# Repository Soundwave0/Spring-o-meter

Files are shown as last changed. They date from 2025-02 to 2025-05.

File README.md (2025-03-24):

## Spring-O-Meter1000
**Ensure that ESP is configured in Arduino IDE with ESPduino package** <br>
https://arduino.esp8266.com/stable/package_esp8266com_index.json <br> in arudino IDE add the following path <br>
# Introduction

Presented here is the device Spring-O-Meter 1000, created for the class FMDII at the faculty of Mechatronics. The aim of this project was to measure the spring constant in both tension and compression springs by building some device. Being a Mechatronic device it contains Electrical, Software and Mechanical Components that work in synchrony. The following documentation will contain a description of the 3 components as well as the usage of the device. For the the Step and Program Files go to  
https://github.com/Soundwave0/Spring-o-meter.git

# Specifications

| Spec | Value | Unit |
|------|-------|------|
| Range Comp. | 90 | mm |
| Range Ten. | 115 | mm |
| MAX Comp pos | 110 | mm |
| MIN Comp. pos | 20 | mm |
| MAX Ten. pos | 135 | mm |
| MIN Ten. pos | 10 | mm |
| Max Comp. Di | 19 | mm |
| Min Comp. Di | 3 | mm |
| MAX force | 9.806 | N |
| MAX cal. weight | 950 | g |
| Min cal. weight | 3 | g |
| Disp per Rotation | 2 | mm |
| Gear Ratio(lead:enc.) | 1:3 |  |
| Encoder Disp. Resolution | 0.022 | mm |
| Force sensor Accuracy | ≈0.1 | % |
| K Accuracy | ≈0.015 | N/mm |

# Usage

1. Download the Spring-O-Meter GUI code either from the git-hub link or install from the executable (if you face any issues in the git-hub version try turning off signing)
2. Plug in the Micro-USB cable into the Spring-O-Meter and then into the USB port in your computer, see if the blue led begins to shine through the support on the bottom. Remember if your Micro-USB cable does not have data transfer capabilities it will turn on but no serial communication will be possible
3. Go to Device Manager-> Ports and check to see if you can see the Silicon Labs CP210x, remember the COM port it is connected to 
4. Launch the GUI and click on "COM Configuration" and select the COM that you found in the previous step
5. Press Check COM if it informs you that everything is good then continue if not restart the application and recheck the COM in device manager
6. If you would like to Calibrate your sensor then turn on Calibration , wait until the button settles then place your Spring-O-Meter on its head then press "Calibrate Zero", after this enter the weight of your test weight then place it, then press "Complete Calibration". Once this button is changed to "Calibrated" continue
7. If you don't want to Calibrate but instead want to use a previous value of Calibration taken from EEPROM, then press Use Prev Cal instead of doing Step 6
8. Next place your Spring-O-Meter in the testing Position, install your spring and press tare, then reset 
9. If you would like to measure the point at which the spring begins to exert a force on the sensor to set your zero better, turn on the kickpoint by pressing the button next to kickpoint label turning the OFF to ON. Move the Stage to tense or compress the spring until the kickpoint is no longer null. Once this happens, move your stage to kick point, tare and reset
10. Now you can begin sampling, move your stage a bit, wait for the measurement to settle then press sample, repeat for desired number of samples then press Graph Spring
11. To reset everything and repeat another trial click New Trial

# Parts

## Stock-Parts

| NAME | SPEC | QTY |
|------|------|-----|
| LSU |  | 1 |
| ESP8266 | NodeMCU 12-E | 1 |
| Encoder 30IMP | KY-040 | 1 |
| Load-Cell 1Kg | NA27 | 1 |
| Load-Cell Amp | HX711 | 1 |
| M2.5x40 |  | 2 |
| M6x12 | ISO4762 | 4 |
| M2.5 pin |  | 1 |
| micro-USB cable | W/ Data Bus | 1 |
| Breadboard cables |  | 12 |

## 3D printed parts

| NAME | SPEC | QTY |
|------|------|-----|
| Spur Gear1 | 3d printed | 1 |
| Spur Gear Clamp | 3d printed | 1 |
| Spur Gear 2 | 3d printed | 1 |
| Base 1 | 3d printed | 1 |
| Base 2 | 3d printed | 1 |
| Base Lid | 3d printed | 1 |
| Cable Lid | 3d printed | 1 |
| Clamp | 3d printed | 1 |
| Plate Big | 3d printed | 1 |
| Plate Small Gear | 3d printed | 1 |
| Plate Small | 3d printed | 1 |

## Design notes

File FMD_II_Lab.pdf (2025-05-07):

### course FMDII

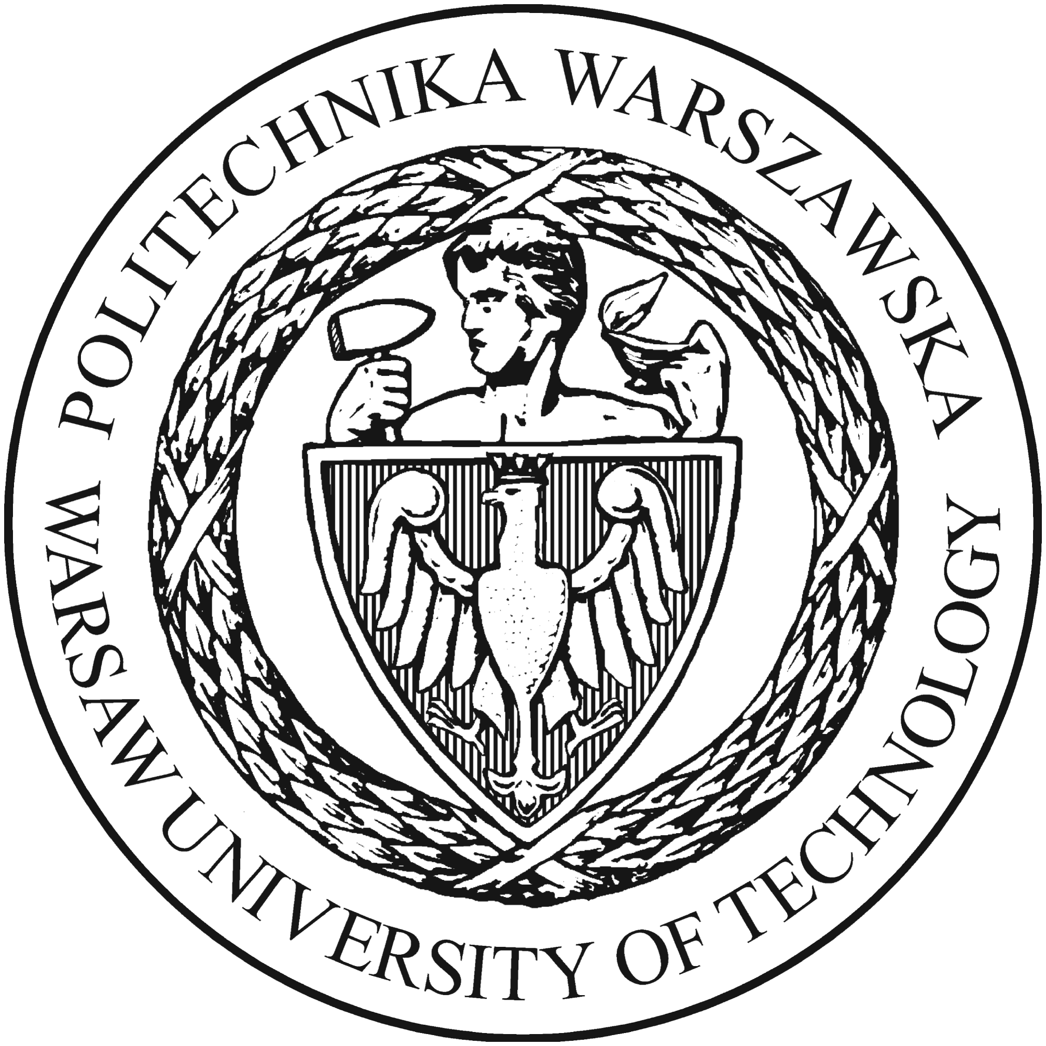
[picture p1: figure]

### Spring-O-Meter 2000

Spring Measurement Device

# Konrad Kosuge, Pawel Seroka

student record book number

supervisor
Dr. Ksawery Sziekedans

WARSAW March 2025

## Contents

1. Introduction | | 2
2. Specifications | | 2
3. Usage | | 3
4. Parts | | 4
4.1. Stock-Parts | | 4
4.2. 3D printed parts | | 4
4.2.1. Spur Gears | | 5
4.2.2. Spur Gear Clamp | | 5
4.2.3. Supports | | 5
4.2.4. Plates | | 5
4.2.5. Clamp | | 5
5. Mechanical Implementation | | 6
5.1. Gearing | | 6
5.2. Force Sensor | | 6
5.3. LSU | | 6
5.4. Mechanism | | 6
6. Electrical Implementation | | 7
6.1. Encoder | | 7
6.2. Force Sensor | | 8

### 7. Software Implementation | 10

7.1. Serial COM Protocol | 10
7.2. ESP 8266 | 11
7.3. GUI | 16
7.4. GUI Backend | 16
7.5. GUI Frontend | 22

### 8. Test | 22

## 1. Introduction

Presented here is the device Spring-O-Meter 1000, created for the class FMDII at the faculty of Mechatronics. The aim of this project was to measure the spring constant in both tension and compression springs by building some device. Being a Mechatronic device it contains Electrical, Software and Mechanical Components that work in synchrony. The following documentation will contain a description of the 3 components as well as the usage of the device. For the the Step and Program Files go to https://github.com/Soundwave0/Spring-o-meter.git

## 2. Specifications

Spec | Value | Unit
Range Comp. | 90 | mm
Range Ten. | 115 | mm
MAX Comp pos | 110 | mm
MIN Comp. pos | 20 | mm
MAX Ten. pos | 135 | mm
MIN Ten. pos | 10 | mm
Max Comp. Di | 19 | mm
MIN Comp. Di | 3 | mm
MAX force | 9.806 | N
MAX cal. weight | 950 | g
MIN cal. weight | 3 | g
Disp per Rotation | 2 | mm
Gear Ratio(lead:enc.) | 1:3
Encoder Disp. Resolution 0.022 | mm
Force sensor Accuracy | ≈0.1 | %
K Accuracy | ≈0.015 N/mm

## 3. Usage

1. Download the Spring-O-Meter GUI code either from the git-hub link or install from the executable (if you face any issues in the git-hub version try turning off signing)
2. Plug in the Micro-USB cable into the Spring-O-Meter and then into the USB port in your computer, see if the blue led begins to shine through the support on the bottom. Remember if your Micro-USB cable does not have data transfer capabilities it will turn on but no serial communication will be possible
3. Go to Device Manager-> Ports and check to see if you can see the Silicon Labs CP210x, remember the COM port it is connected to
4. Launch the GUI and click on "COM Configuration" and select the COM that you found in the previous step
5. Press Check COM if it informs you that everything is good then continue if not restart the application and recheck the COM in device manager
6. If you would like to Calibrate your sensor then turn on Calibration , wait until the button settles then place your Spring-O-Meter on its head then press "Calibrate Zero", after this enter the weight of your test weight then place it, then press "Complete Calibration". Once this button is changed to "Calibrated" continue
7. If you don’t want to Calibrate but instead want to use a previous value of Calibration taken from EEPROM, then press Use Prev Cal instead of doing Step 6
8. Next place your Spring-O-Meter in the testing Position, install your spring and press tare, then reset
9. If you would like to measure the point at which the spring begins to exert a force on the sensor to set your zero better, turn on the kickpoint by pressing the button next to kickpoint label turning the OFF to ON. Move the Stage to tense or compress the spring until the kickpoint is no longer null. Once this happens, move your stage to kick point, tare and reset
10. Now you can begin sampling, move your stage a bit, wait for the measurement to settle then press sample, repeat for desired number of samples then press Graph Spring
11. To reset everything and repeat another trial click New Trial

## 4. Parts

### 4.1. Stock-Parts

NAME | SPEC | QTY
LSU | | 1
ESP8266 | NodeMCU 12-E 1
Encoder 30IMP | KY-040 | 1
Load-Cell 1Kg | NA27 | 1
Load-Cell Amp | HX711 | 1
M2.5x40 | | 2
M6x12 | ISO4762 | 4
M2.5 pin | | 1
micro-USB cable | W/ Data Bus | 1
Breadboard cables | | 12
4.2. 3D printed parts
NAME | SPEC | QTY
Spur Gear1 | 3d printed 1
Spur Gear Clamp 3d printed 1
Spur Gear 2 | 3d printed 1
Base 1 | 3d printed 1
Base 2 | 3d printed 1
Base Lid | 3d printed 1
Cable Lid | 3d printed 1
Clamp | 3d printed 1
Plate Big | 3d printed 1
Plate Small Gear | 3d printed 1
Plate Small | 3d printed 1

4. Parts

### 4.2.1. Spur Gears

Parts (Spur Gear 1 and Spur Gear 2)used in gearing mechanism.

### 4.2.2. Spur Gear Clamp

Clamp is used to fix the Spur Gear 2 onto the screw shaft and prevent it from sliding on the thread by tightening with screws.

### 4.2.3. Supports

Base 1 with Base Lid is used to hide the electronics (amplifier,esp controller). Com-bined with Base 2 it lifts the device so that there is clearance between ground and the moving gears.

### 4.2.4. Plates

Plate Big is used to provide mounting point for the force sensor and to hide cables in the space inside it, closed by the Base Lid.
Plate Small is used as a mounting point for the springs.
Plate Small Gear is used to mount angle sensor with a Spur Gear 1 attached to it.

### 4.2.5. Clamp

Clamp is used to provide attachment point for the springs to the force sensor.

## 5. Mechanical Implementation

### 5.1. Gearing

To measure the rotation of the screw shaft we need to be connect it to the sensor. This can be obtained by using belts, chains or gears. For this project we chose the gear system, due to ease of obtaining gears by 3D printing. Additionally we introduced the gear ratio to improve sensor accuracy. Sensor has 30 impulses per rotation and this causes uncertainty of 12◦
. By introducing a gear ratio equal to 3, we triple the number of pulses per screw shaft rotation. This changes the uncertainty to 4◦

### 5.2. Force Sensor

Force sensor is fixed by screws on to the plate and its purpose is to measure the force applied to the spring.

### 5.3. LSU

Linear stage unit is used to deflect springs with good precision. It acts as a basis in our device to which all the components are mounted. Additionally it enables to maintain the deflection of the spring without additional mechanism.

### 5.4. Mechanism

The idea behind the design is that by turning the threaded shaft the gears are turned with it encoding the rotated angle on the encoder that multiples it by constant (around 0.00185 mm/degree of turn). In this way we obtain the length by which spring is deflected. When the threaded shaft is turned the table is moved and with it the Big Plate causing the offset of the force sensor to which the spring is attached to. This enables the deflection force to be measured. Deflection distance and force information is then sent to the esp controller where it can be processed to provide the spring constant.

## 6. Electrical Implementation

### 6.1. Encoder

KY-040 model, Connecting the Digital Data pins to the ESP and using the CLK to generate the timing pulses to determine the direction of rotation of position for further detail look at the code in the esp8266.

KY-040
Parameter | Specification | Unit
General
Type | Mechanical Incremental Rotary Encoder -
Resolution | 20 pulses per revolution (PPR) | -
Operating Voltage | 5V (3.3V compatible) | V
Current Consumption <10 | mA
Mechanical
Shaft Type | 6mm D-shaped with push button | -
Rotation Life | 100,000 | cycles
Switch Life | 50,000 | cycles
Electrical
Output Type | Quadrature (A/B phase) + Switch | -
Output Signal | Digital (TTL compatible) | -
Debounce Circuit | Included (RC filter) | -
Physical
Module Dimensions | 30 × 19 × 30 | mm
Shaft Length | 15 | mm
Performance
Maximum RPM | 100 | RPM
Contact Resistance | <50 | m
Environmental
Operating Temp | -25 to +70 | °C

Pin Configuration:

1. CLK (A phase output)
2. DT (B phase output)
3. SW (Push button switch)
4. VCC (3.3-5V power supply)
5. GND (Ground)

6. Electrical Implementation

### 6.2. Force Sensor

Load cell NA27 is connected to the HX711 load cell amplifier. The amplifier is connected to the ESP8266 and the code reads the output of the amplifier and determines the force on the sensor. The HX711 interfaces the ESP8266 through the HX711 ADC library. Ensure that the pin that supplies the voltage for the force sensor is the Vin pin since this is the only one that can power 5 Volts. (Force Sensor takes in between 5-12V for proper functionality)

HX711
Parameter | Specification | Unit
General
ADC Type | 24-bit Sigma-Delta | -
Sampling Rate | 10 or 80 (selectable) | SPS
Supply Voltage | 2.6 - 5.5 | V
Operating Current | < 1.5 | mA
Input
Differential Input | ±20mV (PGA=128), ±80mV (PGA=64) | mV
PGA Gain | 128 (default), 64 (selectable) | -
Output
Interface | Serial (2-wire) | -
Data Rate | 10Hz (80Hz noise) or 80Hz (10Hz noise) Hz
Load Cell Support
Excitation Voltage | 5 | V
Recommended Load Cells 1kg, 5kg, 10kg, 20kg | -
Physical
Dimensions | 34 × 17 | mm
Pin Count | 16 | -
Performance
Resolution | 1 in 16,777,216 | counts
Noise (PGA=128) | 0.5 | V RMS ˜
Non-linearity | ±0.01 | % FS
Temperature
Operating Range | -40 to +85 | °C

6. Electrical Implementation

NA27
Rated Capacities | 0.61235610kg
Rated Output | 1.0 ±0.15mV/V
Zero Balance | ±0.1000 mV/V
Non-linearity | 0.03 %R.O.
Hysteresis | 0.03 %R.O.
Repeatability | 0.03 %R.O.
30mins Creep | 0.03 %R.O.
30mins Return | 0.03 %R.O.
Safe Overload | 150 %R.O.
Ultimate Overload | 200 %R.O.
Temperature Effect On Output | 0.01 %R.O./°C
Temperature Effect On Zero | 0.05 %R.O./°C
Input Impedance | 1115±10%
Output Impedance | 1000±10%
Insulation Impedance | 2000 M/(50VDC)
Recommended Excitation | 512 VDC ˜
Maximum Excitation | 15 VDC
OperatingTemperatureRange | -2060 °C ˜
Construction | Aluminum Alloy
Protection Class | IP65
Cable | 0.8×0.25m
Recommended Platform Size | 150×150 mm
Mode of Connection | RedEXC+,BlackEXC-,GreenSIG+,WhiteSIG-

## 7. Software Implementation

### 7.1. Serial COM Protocol

A protocol specifically programmed for this device, the Application can send requests or data over the serial port to the device, and the device can send requests or data over the serial port to the Application. The table features how the Application and the ESP communicate with each other.

Command Description | Expected Response
ONN | Turn on calibration, LED turns on | -
OFF | Turn off calibration, LED turns off | -
WGH | Get the force signal | Force value
POS | Get the position | Position value
IMP | Get the impulse counter | Impulse counter value
COM | Test COM port connection | "OK"
RST | Reset the position | "SUC"
TRE | Tare the scale | "SUC"
CAL | Calibrate the weight | -
TREF | Tare fast during measurement | -
ERR | Error value received when request is invalid | Error message
CALVAL | Change the calibration value in the ESP program -
APUL | Application pulls from microcontroller EEPROM EEPROM data
MPUL | Microcontroller gets value from application | Value from application

7. Software Implementation

### 7.2. ESP 8266

#include<HX711_ADC.h>

#include <EEPROM.h>

//global variables for position encoder
const int pinA = 5;// Connected to CLK on KY040 D1 const int pinB = 4; // Connected to DT on KY040 D2 //global variables for the force sensor
const int pinSCK = 14;//D5
const int pinDT = 12;//D6
//global variables for position encoder functionality

const double impulses = 30;
const double distance_per_rotation = 3.2;//change after measurement

const double gear_ratio = 4;
int encoderPosCount = 0;
int pinALast;
int aVal;
boolean bCW;
const double distance_per_impulse = (1/impulses)*(distance_per_rotation)/gear_ratio;

float plat_pos = 0;
//global variables for force sensor
HX711_ADC LoadCell(pinDT,pinSCK);

boolean _tare = true;
unsigned long t =0;
float calibrationValue =100;
unsigned long stabilizingtime = 3000;//increasing the accuracy of the tare operation by increasing the value

float weight_value = 0;
const int samples = 10;//sampling during filtering and averaging for returning the signal
//global varaibles for communication protocol

String com_data;
// for the EEPROM
double calibrationmap10X5 = 1; //Variable to store data read from EEPROM. int eepromAddress = 0; //address in EEPROM to read and write
int EEPROM_SIZE = 512;//EERPROM SIZE
void encoder_position_reader();//function to read the position of the encoder void com_functions();//function for the communication protocol
void HX711_Loop();//Function for force sensor loop

void setup()
{
pinMode (pinA,INPUT);//Defining pin modes pinMode (pinB,INPUT);

pinMode(LED_BUILTIN, OUTPUT);
pinALast = digitalRead(pinA);
Serial.begin (9600);//Serial begin the Baud rate delay(10);
LoadCell.begin();//Starting the load cell LoadCell.start(stabilizingtime, _tare); LoadCell.setSamplesInUse(samples);
// EEPROM calibration storage EEPROM.begin(EEPROM_SIZE);
}
void loop()
{
com_functions();//Check for communication between application and ESP in serial and respond accordingly encoder_position_reader();//Read encoder position
HX711_Loop();//Read Force
}
void HX711_Loop()
{
LoadCell.update();
weight_value = LoadCell.getData(); }
//Helper Functions
void com_functions()
{
if(Serial.available())
{
com_data = Serial.readStringUntil(’\n’); if(com_data=="ONN")
{
digitalWrite(LED_BUILTIN,LOW); }
else if(com_data == "OFF")
{
digitalWrite(LED_BUILTIN, HIGH); }
else if(com_data == "COM")
{
Serial.write("OK\n");
}
else if(com_data == "XRC") {

}
else if(com_data == "POS") // function to get the position of the platform

{
String myString = String(plat_pos); //Serial.println(plat_pos);
char* buf1 = (char*) malloc(sizeof(char)*myString.length()+1); myString.toCharArray(buf1, myString.length()+1); Serial.write(buf1);
free(buf1);
Serial.write(’\n’);
}
else if(com_data == "IMP")
{
String myString = String(encoderPosCount);
char* buf2 = (char*) malloc(sizeof(char)*myString.length()+1); myString.toCharArray(buf2, myString.length()+1); Serial.write(buf2);
free(buf2);
Serial.write(’\n’);
}
else if(com_data == "RST")//resets the position on the encoder to 0 {

plat_pos = 0;
encoderPosCount = 0;
Serial.write("SUC");
Serial.write(’\n’);
}
else if(com_data == "CALVAL")//pulls the calibration constant from the gui and sets it in the application part {
Serial.write("CALRQS\n");//implement in c# part
//Serial.write(’\n’);
String calibration_value_string = Serial.readStringUntil(’\n’); float calibration_value = calibration_value_string.toFloat();

calibrationValue = calibration_value;
}
else if(com_data == "TRE")//more accuarate slower tare {
LoadCell.tare();
Serial.write("SUC\n");
}
else if(com_data == "CAL")//preforms the calibration operation {
LoadCell.setCalFactor(calibrationValue); Serial.write("SUC");
Serial.write(’\n’);
}

else if (com_data == "TREF")//tare fast {
LoadCell.tareNoDelay();
}
else if(com_data == "WGH")//send the weight {
String myString = String(weight_value); //Serial.println(weight_value);
char* buf3 = (char*) malloc(sizeof(char)*myString.length()+1); myString.toCharArray(buf3, myString.length()+1); Serial.write(buf3);
free(buf3);
Serial.write(’\n’);
}
else if(com_data == "MPUL")//Micro-controller pulls data from application application data -> Micro-Controller {
//send request to application
Serial.write("MAPREQ");//send calibrationmap request to application Serial.write(’\n’);
//receive value
String calibration_value_string = Serial.readStringUntil(’\n’); calibrationmap10X5 = calibration_value_string.toDouble(); //write value to memory
EEPROM.put(eepromAddress,calibrationmap10X5); EEPROM.commit();
}
else if(com_data == "APUL")//Application pulls data from microcontroller Micro-controller -> Application {
double calmap;//write to eeprom when power is on but when off will chnage vlaue to 16711680 (weird) EEPROM.get(eepromAddress,calmap);
String myString = String(calmap);
char* buf = (char*) malloc(sizeof(char)*myString.length()+1); myString.toCharArray(buf, myString.length()+1); Serial.write(buf);
free(buf);
Serial.write(’\n’);
}

else
{
Serial.write("ERR\n");
}
}
}
void encoder_position_reader()

{
aVal = digitalRead(pinA);
if (aVal != pinALast )
{
if (digitalRead(pinB) != aVal) {

encoderPosCount ++;
bCW = true;
}

else
{

bCW = false;
encoderPosCount--;
}
if (bCW){}
else{}

plat_pos = distance_per_impulse*encoderPosCount; }

pinALast = aVal;
}

Above is the code that is flashed to the ESP8266 It contains

1. Setup of the pins
2. Setup of the HX711 Force reading
3. Variables to keep track of the data
4. Encoder position reading
5. Communication Protocol Implementation

### 7.3. GUI

### 7.4. GUI Backend

using System;
using System.Collections.Generic; using System.Collections.Specialized; using System.ComponentModel;
using System.Data;
using System.Diagnostics;
using System.Drawing;
using System.Drawing.Text;
using System.Linq;
using System.Reflection;
using System.Security.Cryptography.X509Certificates; using System.Security.Permissions;
using System.Text;
using System.Threading.Tasks;
using System.Windows.Forms;
using System.Windows.Forms.DataVisualization.Charting;

namespace Spring_o_meter
{

public partial class Form1 : Form
{
//initializing values for calibration
private double signal_zero_state_calibration = 0; private double signal_test_weight_calibration = 0; private double to_force_map = 0;
Boolean calibrated = false;

//initalizing values for reading //idea of using structs for this purpose public struct data_trial
{

public data_trial(double pos, double force) {
Pos = pos;
Force = force;
}
public double Pos { get; set; }
public double Force { get; set; }
}
data_trial current_data = new data_trial();//made null just in case
data_trial prev_data = new data_trial();
Stack<data_trial> data_trial_stack = new Stack<data_trial>();// will store the data in stack format private double spring_k = 0;
private double mean_k = 0;
private double sum = 0;
// for position component
private const double GEAR_RATIO = 3;//between driver and gear
private const double DISTANCE_PER_ROTATION = 2; // distance in mm of distance per rotation private const double IMPULSES_PER_ROTATION = 30;// impulses in the encoder
//for the graph
private const int k_stack_reading_depth = 5;// stack reading depth for graphing trials private Stack<double> stack_k = new Stack<double>(); // stack that stores the spring constants

private int sample_count = 0;
//for the port
private string port = "NULL";
Boolean com_connected = false;
private Boolean kickpoint = false; private Boolean kickpoint_found = false;
private double kickpoint_value = 0.15;
private double sigweight;
private double Impulse_to_position(double encoder_count)

{
return (1 / IMPULSES_PER_ROTATION) * (DISTANCE_PER_ROTATION / GEAR_RATIO) * encoder_count; }
void reset()// implement rest function
{
Get_STM("STM");
}
private void Force_Calibration()
{
if (calibration_Toggle.Text == "ON" && com_connected)

{
serialPort1.WriteLine("WGH");
signal_test_weight_calibration = Convert.ToDouble(serialPort1.ReadLine()); double sigdif = signal_test_weight_calibration - signal_zero_state_calibration; if (double.TryParse(textBox1.Text, out double testweight))//checks if is a double
{
sigweight = testweight / (sigdif);
to_force_map = sigweight * 9.806 / 1000;//now in newtons, gives newtons per sig unit enter_Weight_Button.Text = "Calibrated";
}
else
{
to_force_map = -1;
MessageBox.Show("please enter a valid value", "ERROR", MessageBoxButtons.OK, MessageBoxIcon.Warning); }
}
}
void Graph_K(Chart chartx, String series_name,Stack<data_trial> stack)
{
data_trial[] data_trial_array = stack.ToArray();
SortedDictionary<double,double> keyValuePairs = new SortedDictionary<double,double>(); for (int i =0; i < data_trial_array.Length;i++)
{
double key = Math.Round(Math.Abs(data_trial_array[i].Pos),2);
double value = Math.Round(Math.Abs(data_trial_array[i].Force),2); keyValuePairs.Add(key, value);

}
foreach(var j in keyValuePairs)
{
chartx.Series[series_name].Points.AddXY(j.Key, j.Value); }
}
private double Signal_To_Force(double Signal)
{
return Signal*to_force_map;
}
private String Get_STM(String code) {
if (com_connected)
{
serialPort1.WriteLine(code);
String stm_output = serialPort1.ReadLine(); return stm_output;
}
else
{
MessageBox.Show("COM is not activated", "ERROR", MessageBoxButtons.OK, MessageBoxIcon.Warning); return "ERR";
}

}

private double Get_Position()
{
String imp = (Get_STM("IMP"));
int current_impulse_count = Int32.Parse(imp);
double current_position = (Impulse_to_position(current_impulse_count)); return Math.Round(current_position,5);
}
private double Get_Force()
{
String output = Get_STM("WGH");
double cur_sig = Convert.ToDouble(output);
double current_force = Math.Round(Signal_To_Force(cur_sig), 5); return current_force;
}
private void start_COM(String port_method)
{
serialPort1.PortName = port_method; //make sure to get the right COM serialPort1.Open();//opening the serial port
}
private Boolean Check_COM()
{
if(serialPort1.IsOpen)
{
serialPort1.Close();
}
try
{
start_COM(port);
serialPort1.Write("COM");
//System.Threading.Thread.Sleep(200); string com_status = serialPort1.ReadLine();

if (com_status == "OK")
{
MessageBox.Show("Serial Connected successfully", "PORT NOTIFICATION", MessageBoxButtons.OK, MessageBoxIcon.Information); com_connected = true;
return true;
}
else
{
MessageBox.Show("Correct the COM#", "ERROR", MessageBoxButtons.OK, MessageBoxIcon.Warning); return false;
}
}
catch
{
MessageBox.Show("Correct the COM# big boy error", "ERROR", MessageBoxButtons.OK, MessageBoxIcon.Warning); return false;
}
}
private String COM_dialog()
{
Form2 port_dialog = new Form2(); port_dialog.ShowDialog();
while (port_dialog.finished == false) { } port = port_dialog.port;
return port;
}
private void Graph_Stack(Chart chartx,int stack_reading_depth, Stack<double> stack, String series_name) // fix this function {

Double[] stack_array = stack.ToArray();
double max = -1;
if (chart1.Series.Count != 0)
{
chart1.Series.Clear();
chart1.Series.Add(series_name);

}

for (int i = 0; i < stack_reading_depth; i++) {
if (i<stack_array.Length)
{
double sample_spring_constant = stack_array[i];

if (max < sample_spring_constant) max = sample_spring_constant;

chart1.Series[series_name].Points.AddXY(i, sample_spring_constant); chart1.ChartAreas[0].AxisY.Maximum = max + 0.1 * max; chart1.ChartAreas[0].AxisY.Minimum = 0;
}

else
{
chart1.Series[series_name].Points.AddXY(i, 0); }
}
}
static double standardDeviation(IEnumerable<double> sequence) {
double result = 0;
if (sequence.Any())
{
double average = sequence.Average();
double sum = sequence.Sum(d => Math.Pow(d - average, 2)); result = Math.Sqrt((sum) / sequence.Count());
}
return result;
}
static double Mean(IEnumerable<double> sequence) {
if (sequence.Any())
{
double average = sequence.Average(); return average;
}
return -1;
}

public Form1()
{
InitializeComponent();
timer1.Start();
}

private void Form1_Load(object sender, EventArgs e)//upon loading the form

{

}
private void button1_Click(object sender, EventArgs e)// toggling the {

try
{
if (calibration_Toggle.Text == "OFF")
{
calibration_Toggle.Text = "ON"; calibration_Toggle.BackColor = Color.Green; serialPort1.Write("ONN\n");//turns led on stm on serialPort1.WriteLine("TRE");
if (serialPort1.ReadLine() == "SUC") { }
else
{
MessageBox.Show("STMERROR", "ERROR", MessageBoxButtons.OK, MessageBoxIcon.Warning); }
}
else
{
serialPort1.WriteLine("TRE"); calibration_Toggle.Text = "OFF"; calibration_Toggle.BackColor = Color.Red; serialPort1.Write("OFF\n");
}
}
catch
{
MessageBox.Show("PORT is not configured", "ERROR", MessageBoxButtons.OK, MessageBoxIcon.Warning); }
}
private void button1_Click_1(object sender, EventArgs e)//complete calibration
{
if (calibration_Toggle.Text == "ON" )
{
Force_Calibration();
String response = Get_STM("MPUL");
if (response == "MAPREQ")
{
String to_force_map_string = (to_force_map * 100000).ToString(); serialPort1.WriteLine(to_force_map_string);

}
calibrated = true;
}
else if(calibration_Toggle.Text == "OFF")
{
MessageBox.Show("Turn On calibration", "ERROR", MessageBoxButtons.OK, MessageBoxIcon.Warning); }
}
private void button2_Click(object sender, EventArgs e)//calibrating the self_weight;
{

if (calibration_Toggle.Text == "ON" && !calibrated)
{
serialPort1.WriteLine("CAL");
String output = Get_STM("WGH");
signal_zero_state_calibration = Convert.ToDouble(serialPort1.ReadLine()); button2.Text = "Calibrated";
label23.Text = "LOAD TEST";
label23.BackColor = Color.Green;
}
else if(calibrated)
{
MessageBox.Show("Restart to calibrate", "ERROR", MessageBoxButtons.OK, MessageBoxIcon.Warning); }
else
{
MessageBox.Show("Turn On calibration", "ERROR", MessageBoxButtons.OK, MessageBoxIcon.Warning); }
}
private void button1_Click_2(object sender, EventArgs e)//sampling button add to chart also
{
if (button4.BackColor != Color.Green)
{
MessageBox.Show("calibrate", "ERROR", MessageBoxButtons.OK, MessageBoxIcon.Warning); return;
}
prev_data = current_data;
sample_count++;
current_data = new data_trial(Get_Position(), Get_Force()); data_trial_stack.Push(current_data);
label12.Text = current_data.Pos.ToString();

label13.Text = current_data.Force.ToString(); label14.Text = prev_data.Pos.ToString(); label15.Text = prev_data.Force.ToString();
if (prev_data.Pos == current_data.Pos)
{
MessageBox.Show("change position to attain measurement", "ERROR", MessageBoxButtons.OK, MessageBoxIcon.Warning); return;
}
if (sample_count >= 2)
{
spring_k = Math.Round(Math.Abs((current_data.Force - prev_data.Force) / (current_data.Pos - prev_data.Pos)), 3); sum += spring_k;
mean_k = Mean(stack_k);
label17.Text = spring_k.ToString();
stack_k.Push(spring_k);
try
{
Graph_Stack(chart1, k_stack_reading_depth, stack_k, "K");// to graph the whole thing by displaying }
catch
{
stack_k.Pop();
stack_k.Push(0);
MessageBox.Show("Graph error", "ERROR", MessageBoxButtons.OK, MessageBoxIcon.Warning); }
}
//last 5 measurements from the stack in the form of a line graph
}
private void button3_Click(object sender, EventArgs e)
{
String port_output = COM_dialog();
label4.Text = port_output;
}
private void button4_Click(object sender, EventArgs e) {
if(Check_COM())
{
button4.BackColor = Color.Green; }
else button4.BackColor = Color.Red;
}
private void timer1_Tick(object sender, EventArgs e) {
if (com_connected&&calibrated)
{
double force = Get_Force();
double position = Get_Position();
label20.Text = Math.Round(position,5).ToString()+" mm"; label22.Text = Math.Round(force, 5).ToString()+" N"; if(!kickpoint_found && kickpoint)
{
if(Math.Abs(force) >=kickpoint_value)
{
kickpoint_found = true;
label30.Text = Math.Round(position, 5).ToString() + " mm"; }
}
}
}
private void button5_Click(object sender, EventArgs e) {
serialPort1.WriteLine("TRE");
if (serialPort1.ReadLine() == "SUC") { }
else
{
MessageBox.Show("STMERROR", "ERROR", MessageBoxButtons.OK, MessageBoxIcon.Warning); }
}
private void button6_Click(object sender, EventArgs e)
{
if (Get_STM("RST") == "SUC") { }
else
{
MessageBox.Show("STMERROR", "ERROR", MessageBoxButtons.OK, MessageBoxIcon.Warning); }
}
private void button7_Click(object sender, EventArgs e)
{
Graph_K(chart2,"KC", data_trial_stack);
label25.Text = Math.Abs(Math.Round(sum/(sample_count-1),3)).ToString(); double stand_div = standardDeviation(stack_k.ToArray()); label27.Text= Math.Round(stand_div,5).ToString();
}

private void button8_Click(object sender, EventArgs e)

{
if(button8.Text == "OFF")
{
button8.Text = "ON";
button8.BackColor = Color.Green; kickpoint = true;
}
else
{
button8.Text = "OFF";
button8.BackColor = Color.Red; kickpoint = false;
}
}
private void button9_Click(object sender, EventArgs e)//new trial . resets all values {
stack_k.Clear();
data_trial_stack.Clear();
sum = 0;
sample_count = 0;
label12.Text = "0";
label13.Text = "0";
label14.Text = "0";
label15.Text = "0";
label25.Text = "NULL";
label30.Text = "NULL";
chart1.Series.Clear();
chart1.Series.Add("K");
chart2.Series.Clear();
chart2.Series.Add("KC");

}

private void button10_Click(object sender, EventArgs e)
{
String output = Get_STM("APUL");
double output_normal = Convert.ToDouble(output)/10000000; to_force_map = output_normal;
calibrated = true;
}
}
}

### 7.5. GUI Frontend

Here is how the GUI should look like upon launch

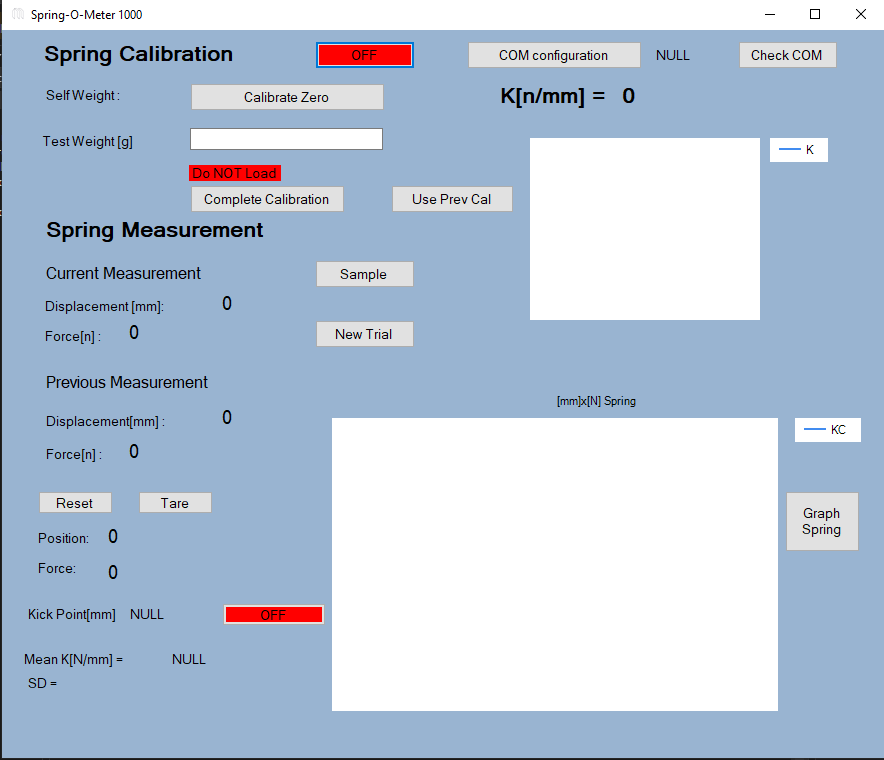
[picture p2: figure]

## 8. Test

K_last K_mean SD
Tension Spring 1 | 0.206 | 0.208 | 0.0074 [N/mm]
Tension Spring 2 | 0.197 | 0.195 | 0.0038 [N/mm]
Compression Spring 1 0.891 | 0.899 | 0.0124 [N/mm]
Compression Spring 2 0.446 | 0.44 | 0.0088 [N/mm]

8. Test

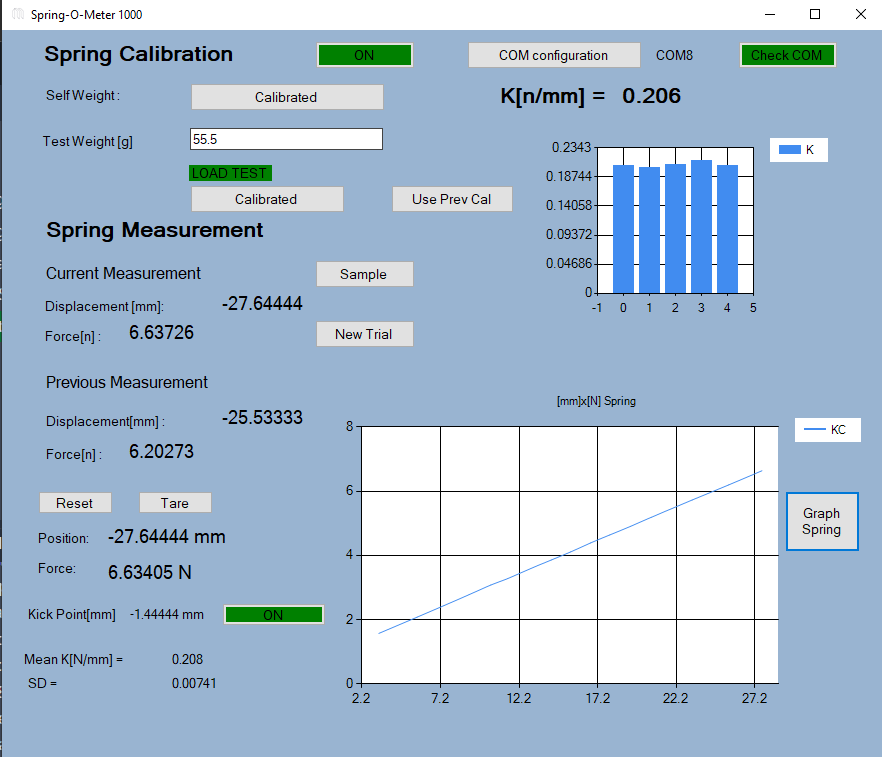
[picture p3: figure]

Figure 8.1. Result for Tension Spring 1 (Shorter)

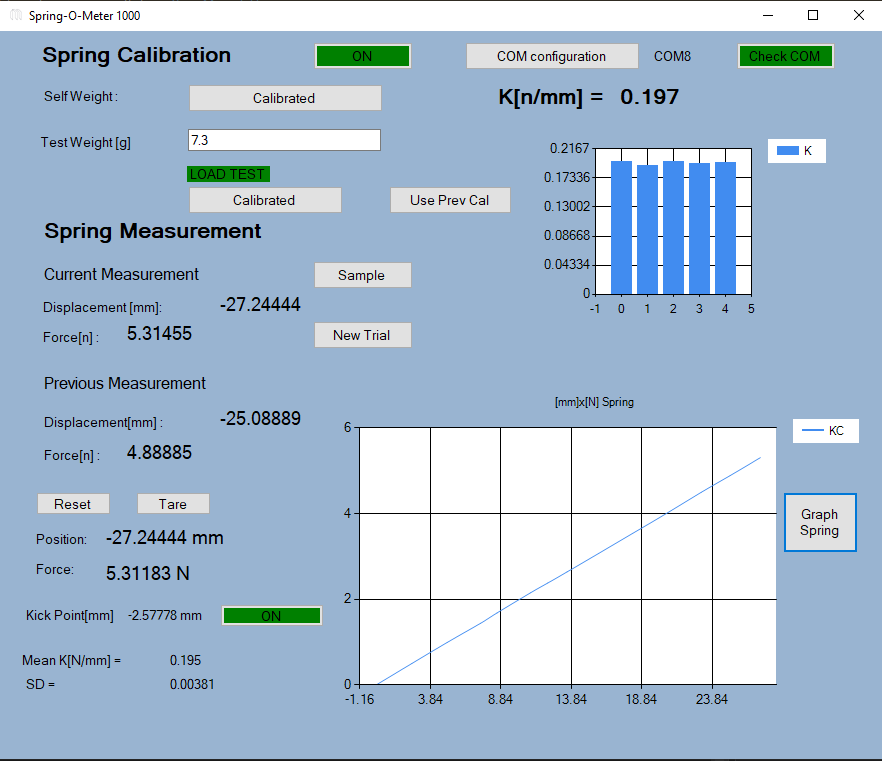
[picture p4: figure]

Figure 8.2. Result for Tension Spring 2

8. Test

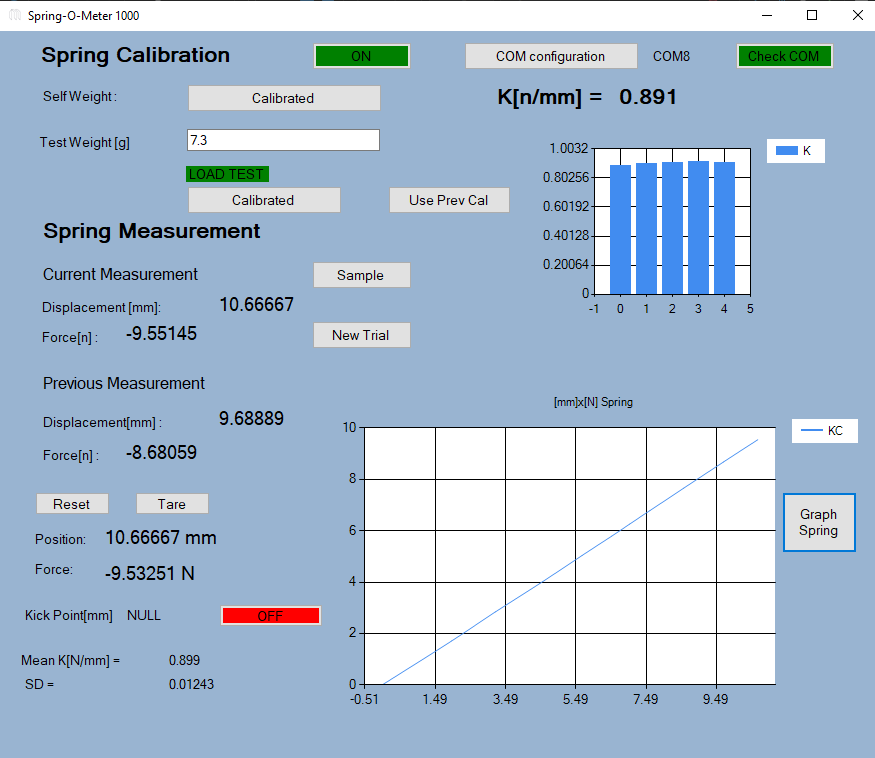
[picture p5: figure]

Figure 8.3. Result for Compression Spring 1

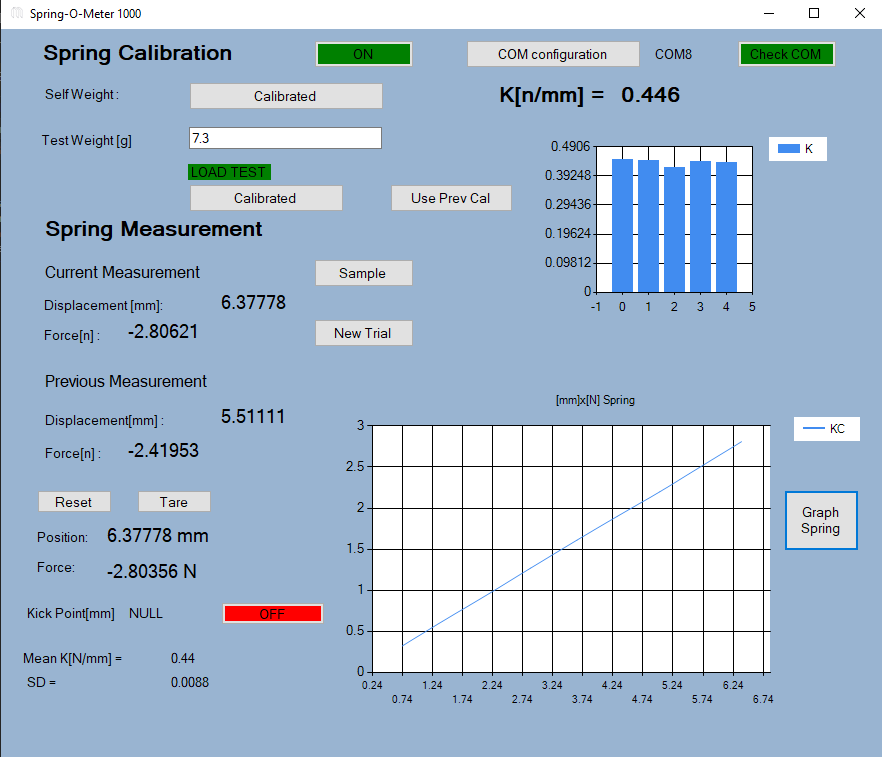
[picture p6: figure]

Figure 8.4. Result for Compression Spring 2 (smaller one)

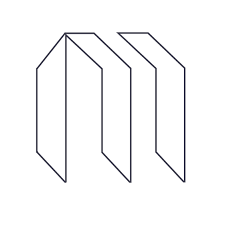
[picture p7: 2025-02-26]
Spring-o-meter/Resources/images.png

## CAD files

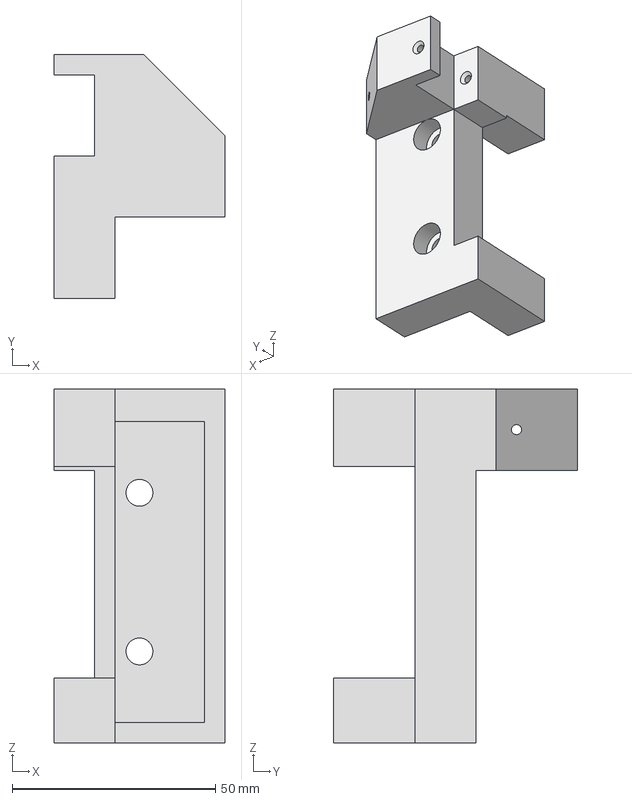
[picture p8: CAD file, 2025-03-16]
step files/plate small.step
42.0 x 60.0 x 87.0 mm

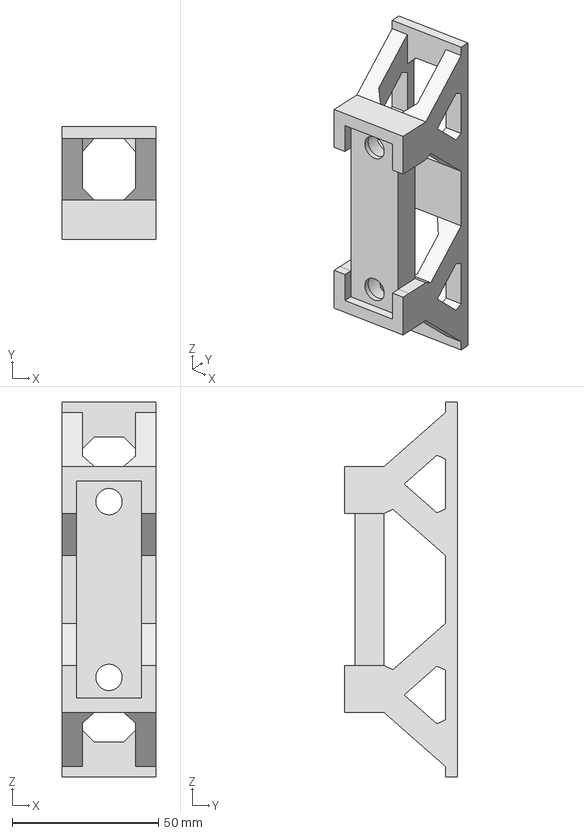
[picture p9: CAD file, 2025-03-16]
step files/base 2.step
32.0 x 38.5 x 128.0 mm

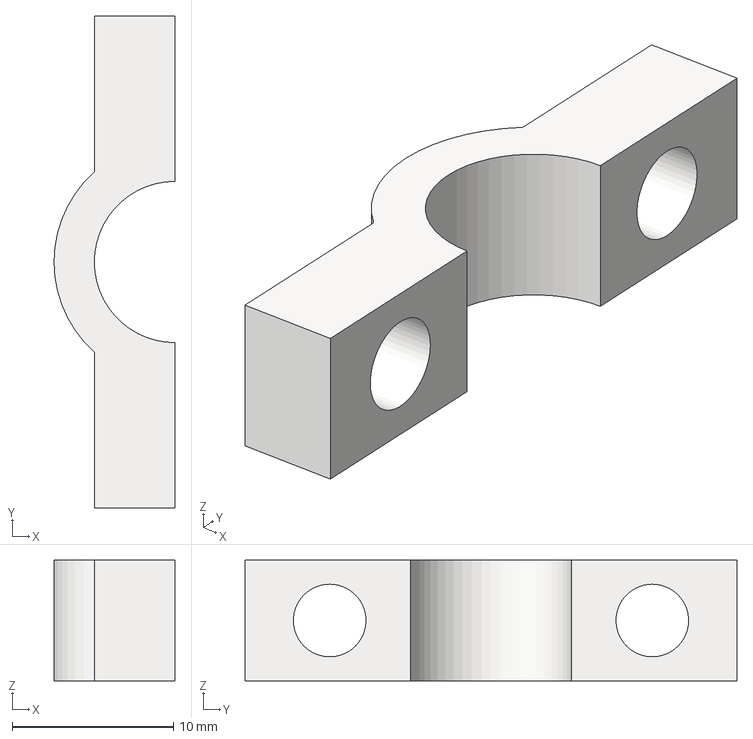
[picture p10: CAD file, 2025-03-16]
step files/Spur Gear22 clamp.step
7.50 x 30.5 x 7.50 mm

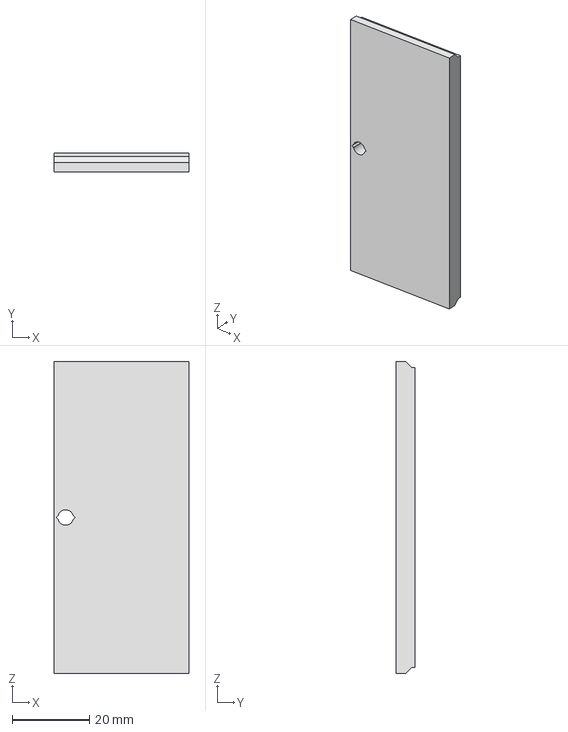
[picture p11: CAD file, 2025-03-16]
step files/base lid.step
35.0 x 5.00 x 81.0 mm

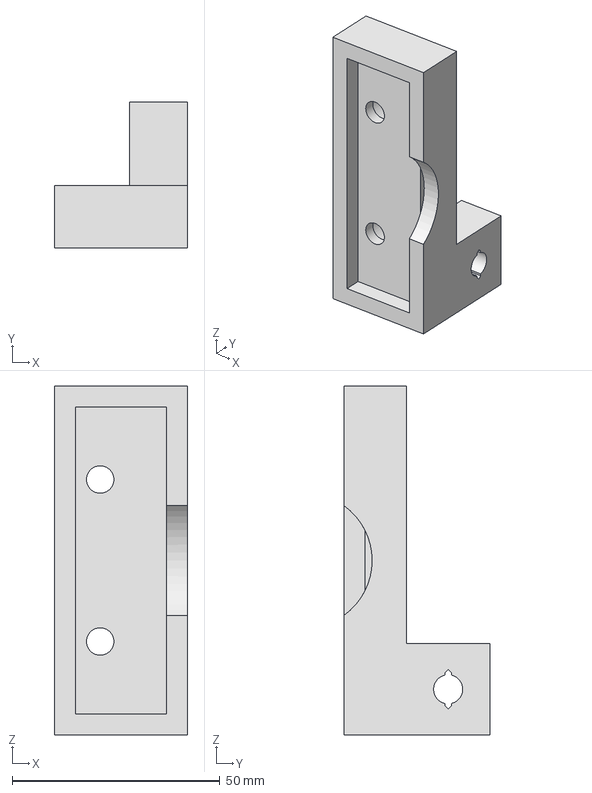
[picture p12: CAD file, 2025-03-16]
step files/plate small gear.step
32.0 x 35.1 x 84.0 mm

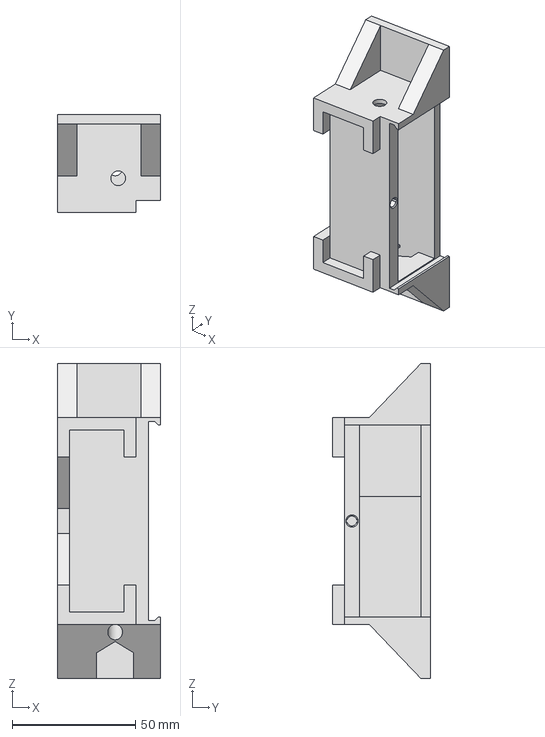
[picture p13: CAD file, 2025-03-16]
step files/base 1.step
42.0 x 40.0 x 128.0 mm

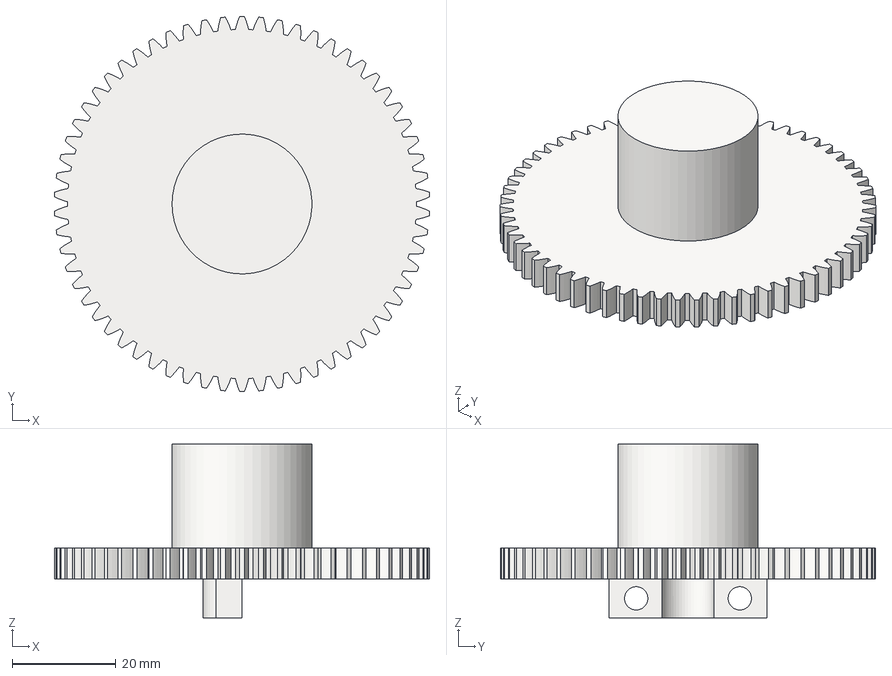
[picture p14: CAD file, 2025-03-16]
step files/Spur Gear22.step
72.4 x 72.4 x 33.5 mm

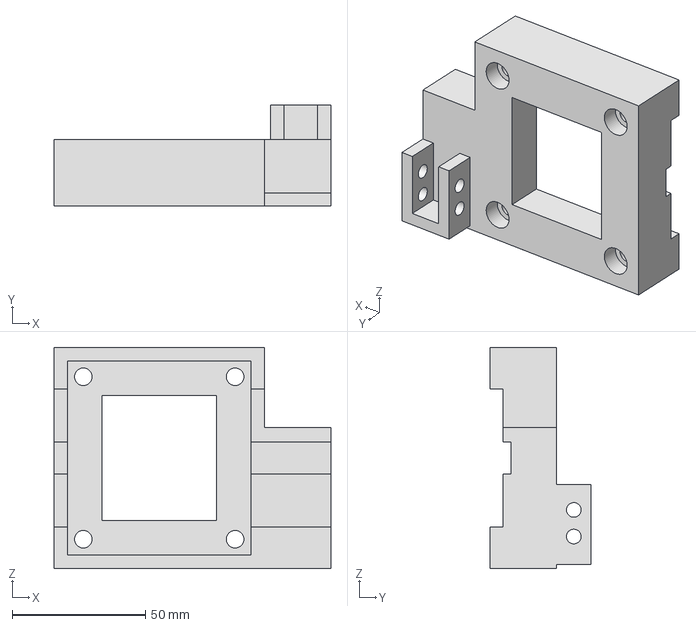
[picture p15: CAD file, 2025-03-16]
step files/plate big.step
104.0 x 38.0 x 83.0 mm

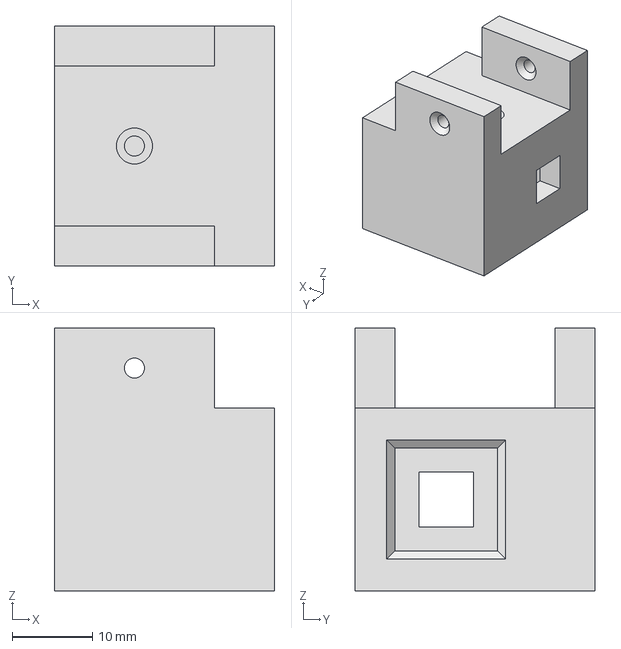
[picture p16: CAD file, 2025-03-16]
step files/clamp.step
27.5 x 30.0 x 32.8 mm

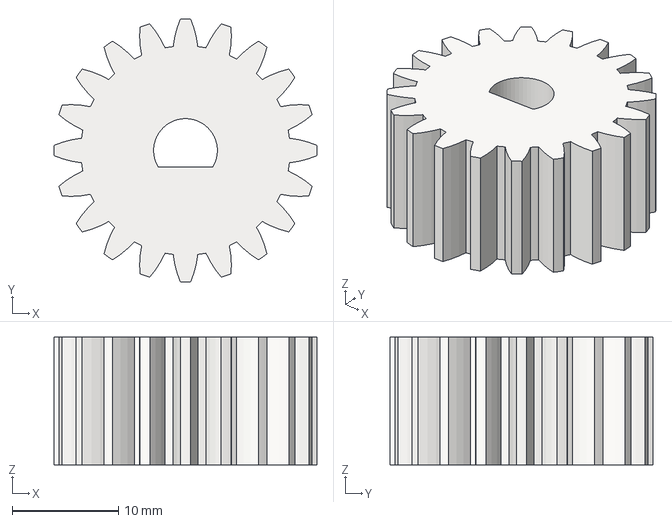
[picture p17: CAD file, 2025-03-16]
step files/Spur Gear12.step
24.7 x 24.7 x 12.0 mm

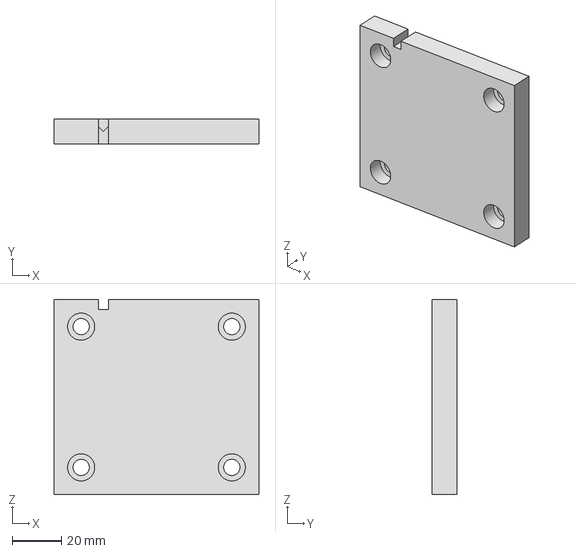
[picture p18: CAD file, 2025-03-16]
step files/cable lid.step
83.0 x 10.0 x 79.0 mm

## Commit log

2025-03-09 force sensor work
2025-03-09 Force sensor overhaul
2025-03-09 graph fixes and optimization, force calibration and reset feautre
